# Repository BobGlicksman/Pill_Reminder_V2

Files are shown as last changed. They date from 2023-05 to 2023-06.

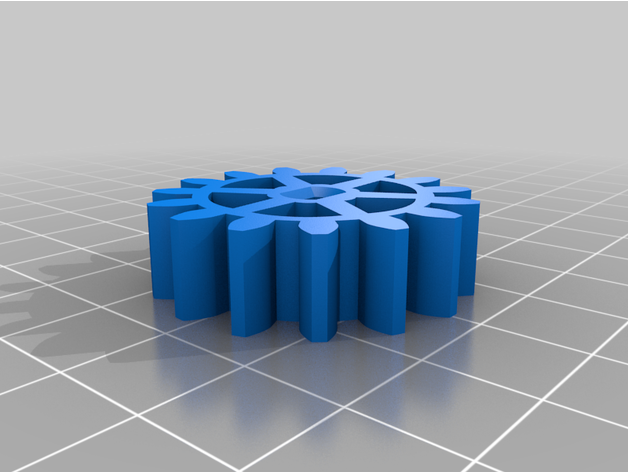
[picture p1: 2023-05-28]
Hardware/_Rotating_Display_table_LITE_5586948/images/Motor_Gear_.png

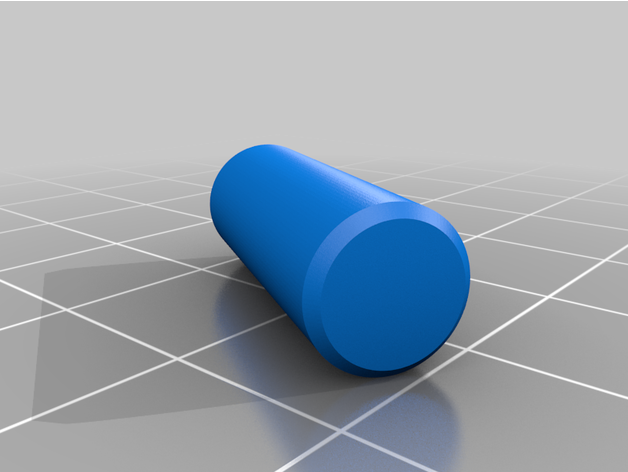
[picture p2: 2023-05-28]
Hardware/_Rotating_Display_table_LITE_5586948/images/Pin_.png

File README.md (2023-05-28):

# Pill_Reminder_V2

A Particle project named Pill_Reminder_V2

## Welcome to your project!

Every new Particle project is composed of 3 important elements that you'll see have been created in your project directory for Pill_Reminder_V2.

#### ```/src``` folder:  
This is the source folder that contains the firmware files for your project. It should *not* be renamed. 
Anything that is in this folder when you compile your project will be sent to our compile service and compiled into a firmware binary for the Particle device that you have targeted.

If your application contains multiple files, they should all be included in the `src` folder. If your firmware depends on Particle libraries, those dependencies are specified in the `project.properties` file referenced below.

#### ```.ino``` file:
This file is the firmware that will run as the primary application on your Particle device. It contains a `setup()` and `loop()` function, and can be written in Wiring or C/C++. For more information about using the Particle firmware API to create firmware for your Particle device, refer to the [Firmware Reference](https://docs.particle.io/reference/firmware/) section of the Particle documentation.

#### ```project.properties``` file:  
This is the file that specifies the name and version number of the libraries that your project depends on. Dependencies are added automatically to your `project.properties` file when you add a library to a project using the `particle library add` command in the CLI or add a library in the Desktop IDE.

## Adding additional files to your project

#### Projects with multiple sources
If you would like add additional files to your application, they should be added to the `/src` folder. All files in the `/src` folder will be sent to the Particle Cloud to produce a compiled binary.

#### Projects with external libraries
If your project includes a library that has not been registered in the Particle libraries system, you should create a new folder named `/lib/<libraryname>/src` under `/<project dir>` and add the `.h`, `.cpp` & `library.properties` files for your library there. Read the [Firmware Libraries guide](https://docs.particle.io/guide/tools-and-features/libraries/) for more details on how to develop libraries. Note that all contents of the `/lib` folder and subfolders will also be sent to the Cloud for compilation.

## Compiling your project

When you're ready to compile your project, make sure you have the correct Particle device target selected and run `particle compile <platform>` in the CLI or click the Compile button in the Desktop IDE. The following files in your project folder will be sent to the compile service:

- Everything in the `/src` folder, including your `.ino` application file
- The `project.properties` file for your project
- Any libraries stored under `lib/<libraryname>/src`

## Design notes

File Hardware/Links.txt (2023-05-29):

Links for Pill Reminder V2 Turntable:

1.  Stepper Motor/Driver:  https://lastminuteengineers.com/28byj48-stepper-motor-arduino-tutorial/
2.  Turntable STL files (remix):  https://www.thingiverse.com/thing:5586948/files
3.  Turntable STL files (original - with parts list, etc.):  https://www.thingiverse.com/thing:4817279
4.  Hall effect sensor (how to use):  https://maker.pro/arduino/tutorial/how-to-use-a-hall-effect-sensor-with-arduino
5.  Hall effect switch from Adafruit:  https://www.adafruit.com/product/158
6.  Hall effect switch from Sparkfun (low voltage and omnipolar):  https://www.sparkfun.com/products/14709
7.  Very small magnet from Sparkfun:  https://www.sparkfun.com/products/8644

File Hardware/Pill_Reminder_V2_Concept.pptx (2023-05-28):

## Pill Reminder V2

Design Concept

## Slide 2

Closed

TOP

Pill Carousel

Open

SIDE

Alignment Pegs

BOTTOM

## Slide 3

TOP COVER

Closed Cover

Carousel rotates under the cover

Open Slot (exposes a pill slot or a closed slot on the carousel, depending upon the time).

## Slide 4

Carousel slots into Platen; Platen rotates the carousel via the gearmotor

PLATEN

TOP

Index holes centered on pill slots

Platen base

Raised mount for carousel

SIDE

Optocoupler

Holes for carousel
Alignment pegs

GearMotor (30 - 60 rpm)

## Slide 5

Design Notes

- Intent is to prevent user from taking pills at the wrong time
  - User can only access pills through a slot at the top
  - Carousel rotates under the top cover to either expose the correct pill slot or else expose the closest of the 4 closed slots, depending upon the pre-set times of day for pill taking.
- Removable Carousel Trays
  - For preparing refills offline
  - Carousel can only insert into Platen one way
  - Platen home position calibrated via a mark on the platen and a setup mode on the app
  - Platen slot exposure traced via opto-coupler and the index holes in the platen.

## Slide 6

Design Notes (2)

- Design based upon Particle device (Photon or Argon or Photon 2)
- App is provided
  - App used for initial position calibration
  - App has a screen for setting # pill taking times per day and the time window for each
- Enclosure houses 16x2 LCD display, red and green LEDs, PIR and (optionally) a piezo buzzer.
  - Carousel moves to proper position during a pill taking time, when the PIR is activated (motion detected near the device)
  - Carousel moves to nearest closed slot when the current pill taking time ends.
  - Red LED lights (flashes) when carousel is moving.
  - Green LED lights (flashes) when pills are under the cover slot and available for taking
  - LCD displays local date/time or messages (pill refill needed, carousel moving, etc.)

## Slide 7

Issues

- Mechanical Calibration: If the Particle device reboots, how does it know where the platen is?
    - Solution #1: There is an initial mechanical (manual) calibration when the unit if first assembled. Thereafter, the Particle device maintains knowledge and tracking of platen position via non-volatile RAM. Position tracking thereafter will be valid until the unit is disassembled and reassembled.
    - Solution #2: Add another index hole or slot at the outside edge of the platen and another opto-isolator to detect it. Now, the Particle device firmware can be used to automatically calibrate each time the device is re-booted and the carousel position tracked using regular volatile RAM.

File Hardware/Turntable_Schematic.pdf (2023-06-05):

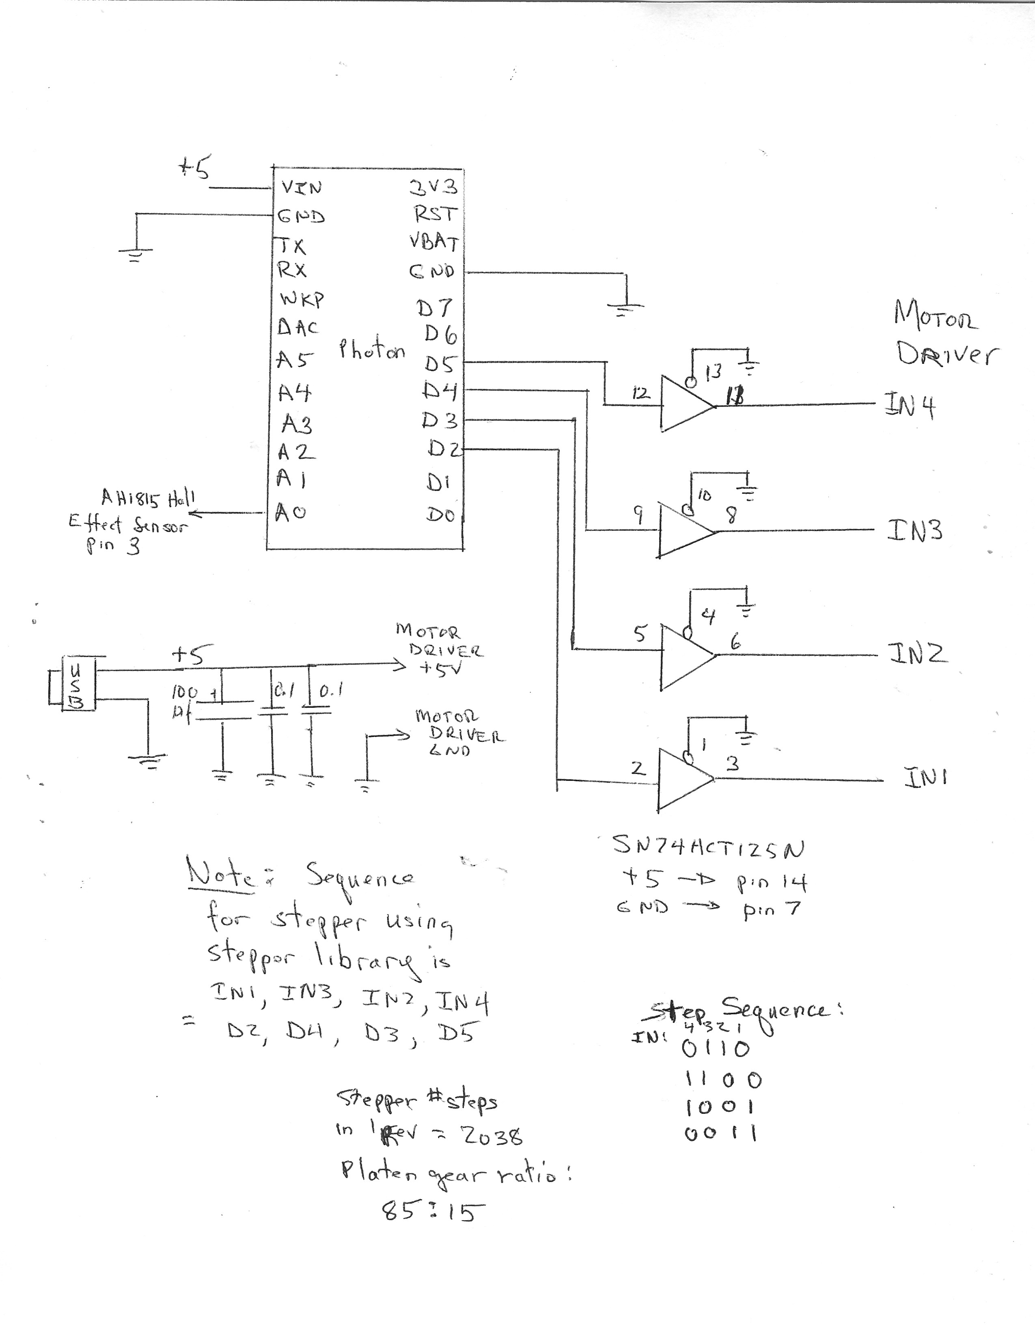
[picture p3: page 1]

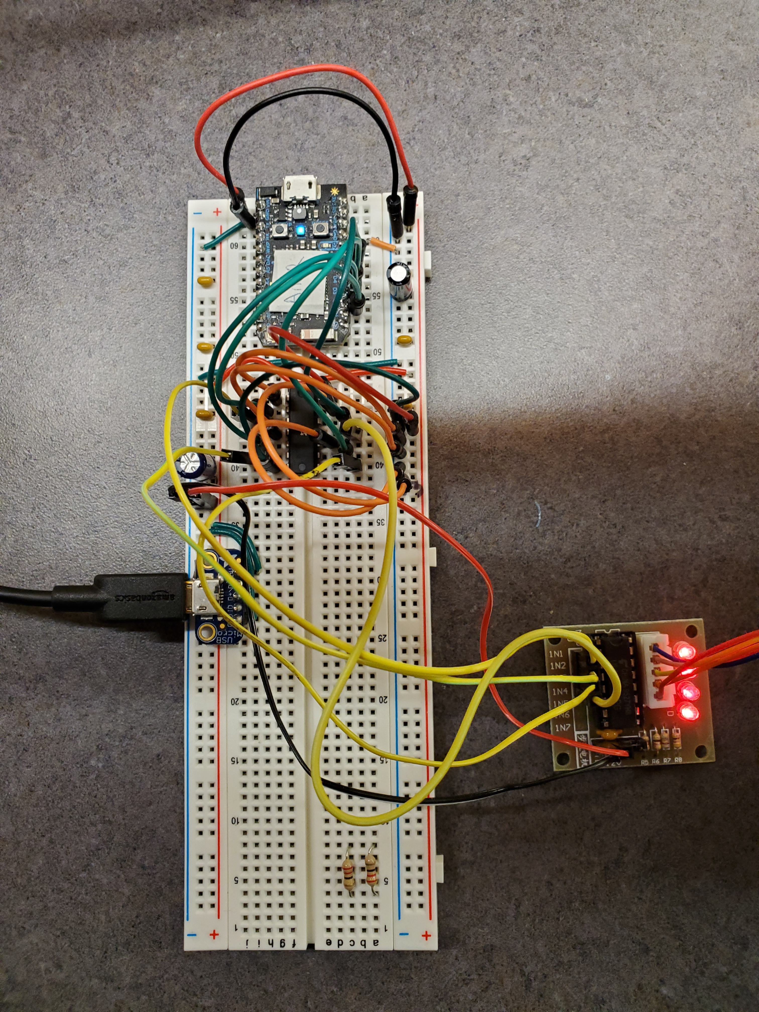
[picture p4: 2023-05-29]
Hardware/Photos/Electronics.jpg

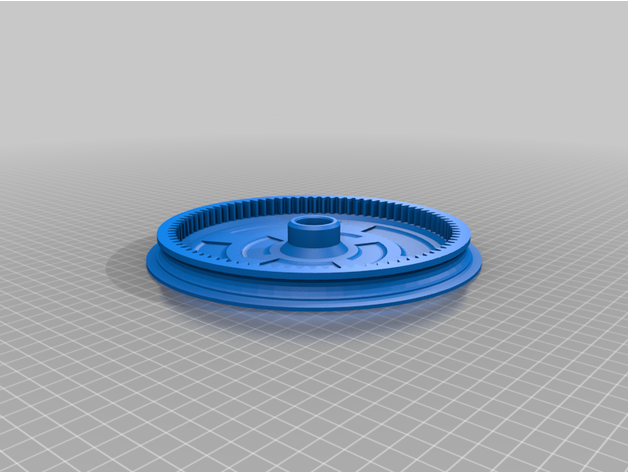
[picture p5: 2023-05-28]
Hardware/_Rotating_Display_table_LITE_5586948/images/Top_plate_.png

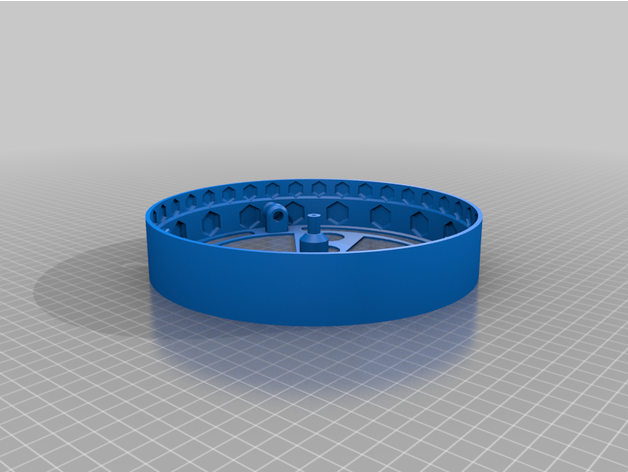
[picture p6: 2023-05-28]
Hardware/_Rotating_Display_table_LITE_5586948/images/Base_covered.png

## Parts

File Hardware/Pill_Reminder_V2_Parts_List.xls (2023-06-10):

PART NAME | VENDOR | PART NUMBER | DESCRIPTION | LINK | QTY | UNIT PRICE | EXTENDED PRICE
Bearing, 608 | Grainger | 608 ZZ PRX | miniature ball bearing, 608 | https://www.grainger.com/product/TRITAN-Miniature-Ball-Bearing-608-49DD47 | 4 | $3.59 | $14.36
Hall Effect Sensor, non-latching | Sparkfun | 14709 | hall effect sensor, AH1815 (non-latching) | https://www.sparkfun.com/products/14709 | 1 | $1.05 | $1.05
magnet, miniature, square | Sparkfun | 8644 | cube magnet, 0.125" | https://www.sparkfun.com/products/8644 | 1 | $1.05 | $1.05
 |  |  |  |  |  |  | $0.00
 |  |  |  |  |  |  | $0.00
 |  |  |  |  |  |  | $0.00
 |  |  |  |  |  |  | $0.00
 |  |  |  |  |  |  | $0.00
 |  |  |  |  |  |  | $0.00
 |  |  |  |  |  |  | $0.00
 |  |  |  |  |  |  | $0.00
 |  |  |  |  |  |  | $0.00
 |  |  |  |  |  |  | $0.00
 |  |  |  |  |  |  | $0.00
 |  |  |  |  |  |  | $0.00
 |  |  |  |  |  |  | $0.00
 |  |  |  |  |  |  | $0.00
 |  |  |  |  |  |  | $0.00
 |  |  |  |  |  |  | $0.00
 |  |  |  |  |  |  | $0.00
 |  |  |  |  |  |  | $0.00
 |  |  |  |  |  |  | $0.00
 |  |  |  |  |  |  | $0.00
 |  |  |  |  |  |  | $0.00
 |  |  |  |  |  |  | $0.00
 |  |  |  |  |  |  | $0.00
 |  |  |  |  |  |  | $0.00
 |  |  |  |  |  |  | $0.00
 |  |  |  |  |  |  | $0.00
 |  |  |  |  |  |  | $0.00
 |  |  |  |  |  |  | $0.00
 |  |  |  |  |  |  | $0.00
 |  |  |  |  |  |  | $0.00
 |  |  |  |  |  |  | $0.00
 |  |  |  |  |  |  | $0.00
 |  |  |  |  |  |  | $0.00
 |  |  |  |  |  |  | $0.00
 |  |  |  |  |  |  | $0.00

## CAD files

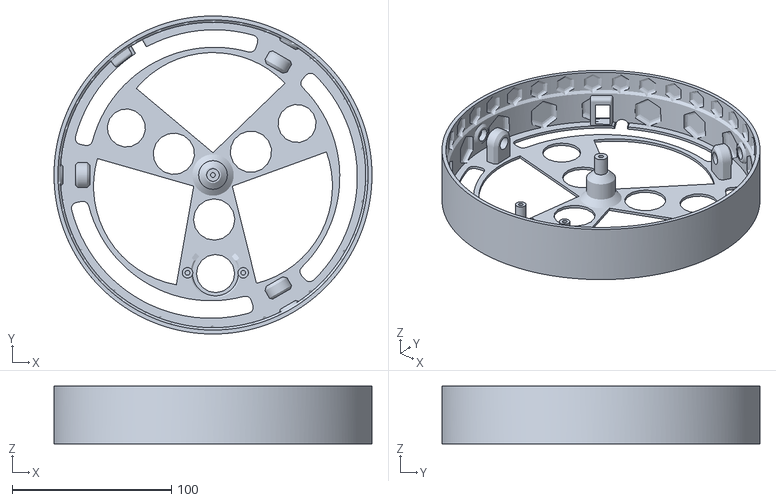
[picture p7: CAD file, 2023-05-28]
Hardware/_Rotating_Display_table_LITE_5586948/files/Base_covered.stl
200.0 x 200.0 x 36.5

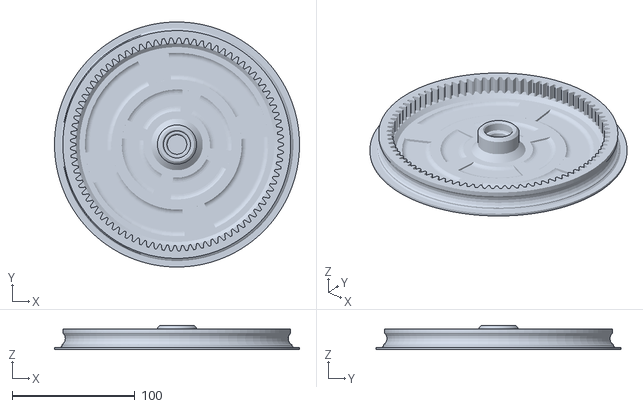
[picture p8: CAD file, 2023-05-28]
Hardware/_Rotating_Display_table_LITE_5586948/files/Top_plate_.stl
200.0 x 200.0 x 20.0

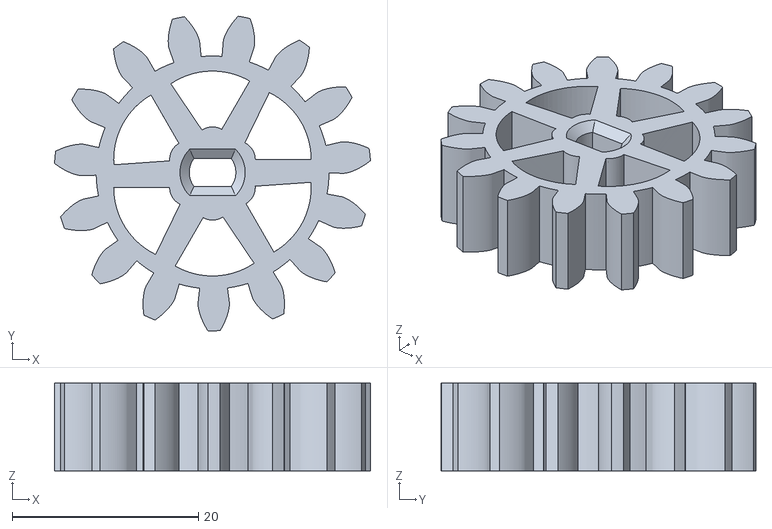
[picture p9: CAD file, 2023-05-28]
Hardware/_Rotating_Display_table_LITE_5586948/files/Motor_Gear_.stl
33.9 x 33.8 x 9.42

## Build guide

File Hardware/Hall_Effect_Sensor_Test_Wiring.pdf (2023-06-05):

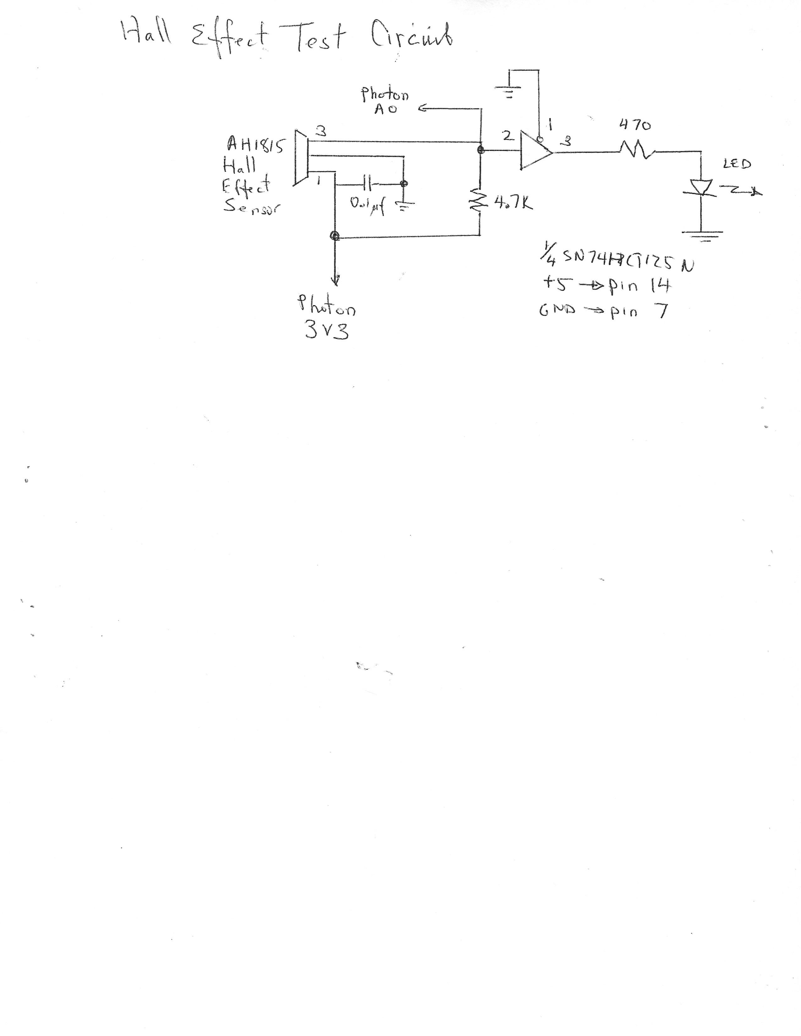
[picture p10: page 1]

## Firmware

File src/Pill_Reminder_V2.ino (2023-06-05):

/*
 TURNTABLE TEST PROGRAM

 This program drives a 28BYJ-48 unipolar stepper motor with UNL2003 quad darlington driver.
 The number of steps in a full rotation is calculated to be:
 - Basic stepper: 32 
 - Stepper internal gearing: 63.68395
 - turntable gearing: 5.66666....  (85:15)

 This program uses the Arduino stepper library and runs on a Particle Photon. Photon pins
 D2, D3, D4 and D5 are wired to stepper motor driver IN1, IN2, IN3 and IN4, respectively, through
 3.3 volt to 5 volt converters (SN74HCT125N).

 Note that for these unipolar stepper motors to work, the motor lead sequnce to the library
 constructor must be IN1, IN3, IN2 and IN4, that this exact sequence.

 The main purpose of this test program is to test proper control of the stepper and assess
 the maximum turntable speed that can be achieved.  The parameter to set the speed of stepping
 is the global constant "delayTime" (value in milliseconds).  

 The program turns the turntable one full revolution clockwise and then one full revolution
 counter-clockwise with a 500 ms delay between direction reversals.  The program repeats 
 indefinitely.

  version 1.1; 6/5/2023;  Added hall effect sensor and home the platen on each loop.
  version 1.0, 5/29/2023:  Initial release for testing

 (c) 2023; by: Bob Glicksman, Jim Schrempp, Team Practical Projects
 All rights reserved.

 */

#include <Stepper.h>

SYSTEM_MODE(AUTOMATIC);
SYSTEM_THREAD(ENABLED);

const int stepsPerRevolution = 2038;  // not needed in this test code
const int delayTime = 2000;  // The smallest delay that the stepper will work (in microseconds))!
const int stepsInOneDirection = 11548; // 32 * 63.68395 * 5.6666...
const int stepsForNextSlot = 722; // 1/16 of the way around

// initialize the stepper library, sequence is IN1, IN3, IN2, IN4 on pins D2 through D5:
Stepper myStepper(stepsPerRevolution, D2, D4, D3, D5);  // note the pin sequence in the constructor!

void setup() {
  // the stepper library does all of the needed pinMode() stuff for the stepper.
  pinMode(A0, INPUT); // Pin to read the Hall Effect Sensor for home position
  
}

void loop() {
  // first thing - home the platen
  seekHome();
  delay(2000);  // pause to indicate that we are homed

  // step forward for one slot:
  for(int i = 0; i < stepsForNextSlot; i++)  {
    myStepper.step(1);
    delayMicroseconds(delayTime);
  }
  // pause
  delay(500);

// step forward for one slot:
  for(int i = 0; i < stepsForNextSlot; i++)  {
    myStepper.step(1);
    delayMicroseconds(delayTime);
  }
  // pause
  delay(500);  

  // step backward for one slot:
  for(int i = 0; i < stepsForNextSlot; i++)  {
    myStepper.step(-1);
    delayMicroseconds(delayTime);
  }
  // pause before homing
  delay(500);

}

// function to home the sensor
//  The home position is where the Hall Sensor output goes LOW
void seekHome() {
  while (digitalRead(A0) == HIGH) {  // the position is not home, so step
    myStepper.step(1);  // take one step clockwise
    delayMicroseconds(delayTime);
  }

  // we are at the home position
  return;
} // end of seekHome()

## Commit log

2023-05-28 Added hardware related files
    [Base_covered.stl, Motor_Gear_.stl, Pin_.stl, Top_plate_.stl]
2023-05-29 Update Links.txt
    Added link for Hall Effect sensor tutorial.
2023-05-29 Enabled the system thread
2023-05-29 Update Pill_Reminder_V2.ino
    Updated comments to get the right pin numbers.
2023-05-29 Update Links.txt
    Added link for hall effect sensor from Adafruit.
2023-05-29 Added links for hall effect sensor and magnet
2023-06-05 Version 1.1
    Added the Hall Effect Sensor (Photon A0). Modified loop() to (a) home the platen and wait 2 seconds, (b) step forward 1/16 rev, (b) step forward 1/16 rev, (c) step backward 1/16 rev, then home again 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
2023-06-05 Updated schematics
    Updated the turntable schematic for show connection of Hall Effect sensor to A0. Added schematic for the hall effect sensor and LED indicator.
2023-06-10 Create Pill_Reminder_V2_Parts_List.xls
    Started a parts list
    [Pill_Reminder_V2_Parts_List.xls]
